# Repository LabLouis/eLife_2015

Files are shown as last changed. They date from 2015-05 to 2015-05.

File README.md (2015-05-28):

Title: Dynamical feature extraction at the sensory periphery guides chemotaxis (manuscript submitted to eLIFE)

Authors: Schulze, A., Gomez-Marin, A., Rajendran, V. G., Lott, G., Musy, M., Ahammad, P., Deogade, A., Sharpe, J., Riedl, J., Jarriault, D., Trautman, E. T., Werner, C., Venkadesan, M., Druckmann, S., Jayaraman, V. and M. Louis

Overview:

This folder contains the scripts for software and design and layout of the hardware associated with the Schulze et al. eLife 2015 manuscript. The repository is organised into five modules corresponding to the specific tools described in the manuscript. Below is a brief description of each module:

1. Electrophysiolgy: Contains scripts associated with the electrophysiology protocols used in the paper.
2. Spike Sorting (OpSIN): Contains scripts and examples associated with the optogenetics-based spike sorting of the electrophysiology data.
3. Tracker Hardware: Contains design files (CAD format) and inventory for the hardware associated with the high-resolution larval tracker.
4. Wormsign: Contains C++ scripts for the software to conduct experiments at the high-resolution larval tracker.
5. Venkman: Independent software module which is used to define the spatial and temporal virtual olfactory environments tested at the larval tracker. This module is coupled to the Wormsign module.

For further details, please find the README file corresponding to each module. For comments/feedback, please e-mail: mlouis_at_crg.eu or matthieu.louis_at_icloud.com

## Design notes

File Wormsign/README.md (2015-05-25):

##Wormsign
####Closed Loop Larva Virtual-Olfaction-Reality System

This software is responsible for the real-time: 

    1) Image analysis with larvae tracking,
    2) Light stimulus delivery, and 
    3) Data acquisition.

######Software Developed By:
Gus K Lott III, PhD, PMP
lottg@janelia.hhmi.org
April 2011

######Software Developed At:
HHMI Janelia Research Campus
19700 Helix Dr.
Ashburn, VA, USA 20147

######Larva Tracker Project Team:
Science: Matthieu Louis, Vivek Jayaraman, Alex Gomez-Marin, Vani Rajendran
Engineering: Gus Lott, Eric Trautman, Lakshmi Ramasamy, Magnus Karlsson, Chris Werner, Pete Davies

For bug reports/comments/feedback, e-mail: mlouis_at_crg.eu or matthieu.louis_at_icloud.com

MAIN.CPP function launches the application GUI (defined in wormsign.h) and sets the windows priority class to REALTIME.  It then initializes the Qt event monitoring loop (in QApplication) which handles button-presses and graphics draw updates, etc.

###The application is structured as several concurrent processes:

    1) Main GUI Thread - defined in wormsign.h
    2) Camera Interface Thread - captures images and does analysis
    3) Stimulus Thread - monitors camera thread for analysis results and sends stimulus
    4) Stage Thread - Communicates with Zaber stages to keep track of current stage position and to track the animal
    5) Experiment Agent Thread - Coordinates the execution of the experiment and carries out data logging

###Wormsign must interconnect with the following systems:

    1) "Venkman" biorules server application (network socket)
    2) Four Zaber Stages (single serial interface)
    3) Stimulus delivery and Camera triggering embedded system (single serial interface)
    4) Basler A622fm Video Camera (IEEE 1394 w/ Basler Pylon Drivers installed)

###This application relies upon the following external software libraries:

    1) Developed under Windows 7 using the windows SDK
    2) Qt v4.7 Application Development Framework
    3) OpenCV v2.2 Computer Vision Library
    4) Basler Pylon v2.3 Camera Interface API

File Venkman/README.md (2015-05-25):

Venkman 

Software Developed By:
Scientific Computing Group
HHMI Janelia Research Campus, Ashburn, VA, USA

For bug reports/comments/feedback, e-mail: mlouis_at_crg.eu or matthieu.louis_at_icloud.com

=======

##Overview

Venkman allows researchers to create “bio-rules” - olfactory experience paradigms based on a larva's current behavior.  
Several bio-rules are supported, enabling a multitude of virtual reality paradigms that broadly fall into categories of time-based, position-based, and/or behavior-based protocols.  
Venkman does this by interfacing with the Wormsign tracking application.  

The following diagram depicts the high level hardware and software components in the system:
 
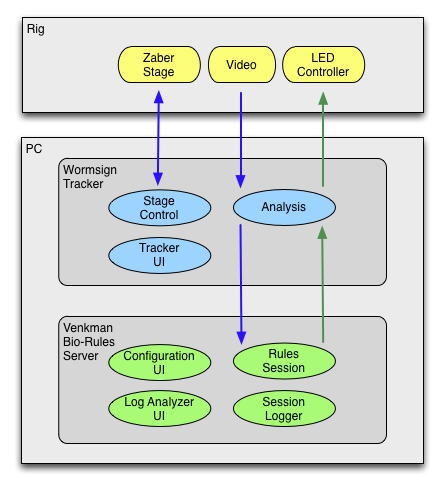
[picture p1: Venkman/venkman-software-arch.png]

 
The bio-rules server accepts body-state measurements such as head, neck and tail positions, head to body angle, and tail bearing from the Wormsign computer vision and tracking algorithm.  
Depending on the VR paradigm chosen by the user for the experiment, these data are used to determine the appropriate stimulus intensity for the current frame.  
The stimulus information is then sent back to Wormsign, which relays the command to the LEDs.
 
##Code / Build Process
 
Venkman is written in Java and was developed using the [IntelliJ IDE](https://www.jetbrains.com/idea/).

IntelliJ should be used to compile and run automated tests.
An ant target 'jar-server' can be used to bundle the compiled results into a jar for deployment.
  
##License

Use is subject to Janelia Research Campus Software Copyright 1.2 license terms 
( [http://license.janelia.org/license/janelia_copyright_1_2.html](http://license.janelia.org/license/janelia_copyright_1_2.html) ).

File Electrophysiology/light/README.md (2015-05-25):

**********************************************
LED_Light_Stimulation.vi: Execution of light stimulation protocols to evoke neural activity in ChR2 expressing neurons according to a preconceived stimulation file (csv format).

By Vani Rajendran and Aljoscha Schulze
Center for Genomic Regulation (CRG), Barcelona Spain
AljoschaTobias@yahoo.com

For bug reports/comments/feedback, e-mail: mlouis_at_crg.eu or matthieu.louis_at_icloud.com
**********************************************

This package contains a Labview routine to drive an LED stimulation according to to a preconceived light stimulation time course (in the form of voltage values defining the light intensity). This stimulation protocol was used in conjunction with one 'NI USB-6008 12-Bit, 10 kS/s Low-Cost Multifunction DAQ' board connected to a PC. The analog output of this DAQ board was connected to the LED driver driving changes of the LED intensity according to the light stimulation protocol.In order to learn the relationship between the output voltage and the light intensity present at the experimental setup, a calibration of the LED as it is connected to the LED controller has to be performed prior to running this routine.

The light stimulation protocol should come in the form of a csv file containing only one column of voltage values. Every line in this csv file corresponds to a voltage and thus a light intensity value of the stimulation time course (values should not exceed 5V). The frame-size (Set frame size) of the execution protocol has to be defined before the stimulation is executed at the Labview VI front panel by the user (units are in milliseconds).

For bug reports/comments/feedback, e-mail: mlouis_at_crg.eu or matthieu.louis_at_icloud.com

**********************************************
Main routines:
**********************************************

* LED_Light_Stimulation.vi: LED stimulation interface

Execution of this program leads to the execution of custom LED stimuli via the analog output port of a Multifunction DAQ device. The stimulus time course (voltage values) of the odor channel has to be computed prior to the execution and saved as a csv file. The user should adapt the stimulation protocol to the frame-size that he intends to use. 

**********************************************
Front panel:
**********************************************

Stimulation START: Pressing this button leads to a prompt asking the user to load the stimulation csv file. As soon as the file is selected the stimulation starts.

Set frame size (min=2ms): Define the frame size of the stimulation protocol in units of milliseconds.

Duration of the Stimulation (s): Shows the duration of the stimulation protocol for the defined frame-size.

Length of csv file: Shows the number of values (each values corresponding to a single frame of the stimulation) contained in the loaded stimulation csv file.

Format of the csv file: The csv file should contain only one column of numbers (voltage values) that correspond to the LED stimulation.

**********************************************
Block diagram:
**********************************************

The user has to open the DAQ Assistant and edit both the coordinates and the analog output port of the DAQ device that is being used to drive the light stimulation via the LED controller.

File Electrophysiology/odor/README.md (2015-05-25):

**********************************************
Odor_stimulation.vi: Execution of odor stimulation protocols to evoke neural activity according to a preconceived stimulation file (csv format).

Software Developed By:
Aljoscha Schulze
Center for Genomic Regulation (CRG), Barcelona, Spain
AljoschaTobias@yahoo.com

For bug reports/comments/feedback, e-mail: mlouis_at_crg.eu or matthieu.louis_at_icloud.com
**********************************************

This package contains a LabView routine to drive a dynamic air-flow/odor stimulation according to a preconceived odor stimulation time course that contains voltage values defining the corresponding to the air-flow in each channel. The stimulation execution is defined in such a way as to have the combined flow of both channels never exceed a predefined value. As a result the combined flow of both channels is kept constant.

This two channel stimulation protocol was used in conjunction with one 'NI USB-6008 12-Bit, 10 kS/s Low-Cost Multifunction DAQ' board connected to a PC. Each of the two analog outputs of this DAQ board was connected to an air-flow controller driving changes of the air-flow according to the loaded stimulation protocol. In order to learn the relationship between the output voltage and the achieved air-flow/odor concentration a calibration of the flow controller (by measuring the air-flow and/or the resulting odor concentration) has to be performed before running this routine. 

The odor stimulation protocol has to come in the form of a csv file containing one column of voltage values (corresponding the values driving the air-flow controller of the odor channel). Every line in this csv file corresponds to a voltage and thus a flow value of the odor stimulation (values should not exceed 5V). The frame-size (Set frame size) of the execution protocol has to be defined before the stimulation is executed at the LabView VI front panel by the user (units are in milliseconds).

**********************************************
Main routines:
**********************************************

* Odor_stimulation.vi: Two channel odor stimulation interface

Execution of this program leads to the execution of custom air-flow/odor stimuli via two channels of the analog output port of a Multifunction DAQ device. The stimulus time course (voltage values) has to be computed prior to the execution and saved as a csv file. The empty channel is continuously computed by subtracting the voltage values of the odor channel from the user defined maximum flow rate. The user should adapt the stimulation protocol (csv file) to the frame-size that he intends to use.

**********************************************
Front panel:
**********************************************

Stimulation START: Pressing this button leads to a prompt asking the user to load the stimulation csv file. As soon as the file is selected the stimulation starts.

Set frame size (min=2ms): Define the frame size of the stimulation protocol in units of milliseconds.

Set maximum voltage: Define the voltage corresponding to the combined flow of channel 1 + channel 2. As a result the flow will always be kept at this constant value throughout the stimulation.

Duration of the Stimulation (s): Shows the duration of the stimulation protocol for the defined frame-size.

Length of csv file: Shows the number of values (each values corresponding to a single frame of the stimulation) contained in the loaded stimulation csv file.

Format of the csv file: The csv file should contain only one column of numbers (voltage values) that define the flow rate of the odor-channel. The values driving the complementary (empty) channel are derived by subtracting the odor channel from the defined overall flow ('maximum voltage').

**********************************************
Block diagram:
**********************************************

The user has to open the DAQ Assistant and edit both the coordinates and the analog output port of the DAQ device that is being used to drive the light stimulation via the LED controller.

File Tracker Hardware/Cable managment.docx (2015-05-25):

The purpose of this document is to document the umbilical handling and support system used for the larva tracker. The following pictures show the umbilical handling approach. A cable guide by IGUS was used to control the camera and blue LED lighting cables (model number of the cable guide is provided in the BOM).

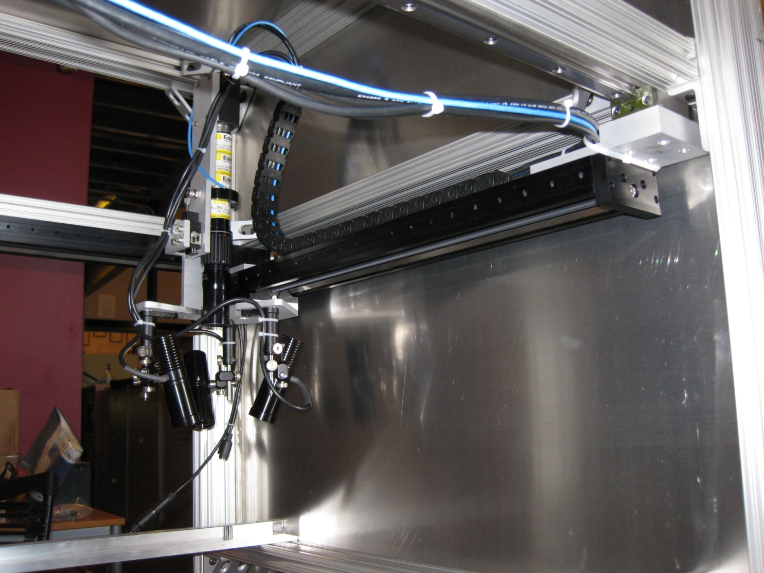
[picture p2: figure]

IGUS Cable guide was attached to and resting on the top side of the Zaber rail. The guide was anchored to the Zaber at this point.

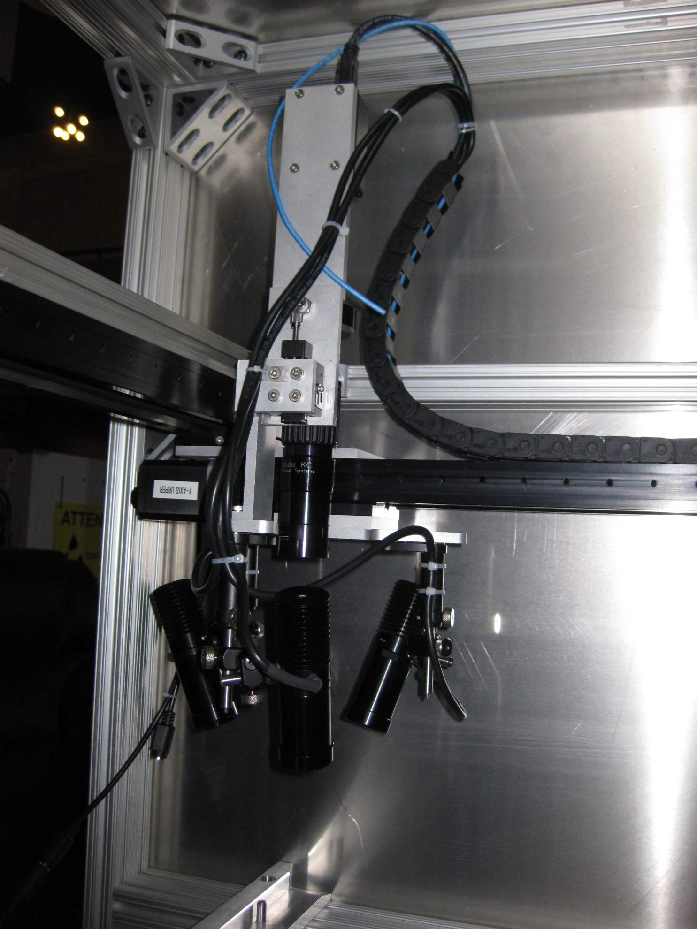
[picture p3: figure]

A two conductor, shielded wire was added to the assembly to trigger the camera (per HHMI request).

Cabling was tie-wrapped and anchored to mounting plates for strain relief.

IGUS Cable guide was about 20 inches long.

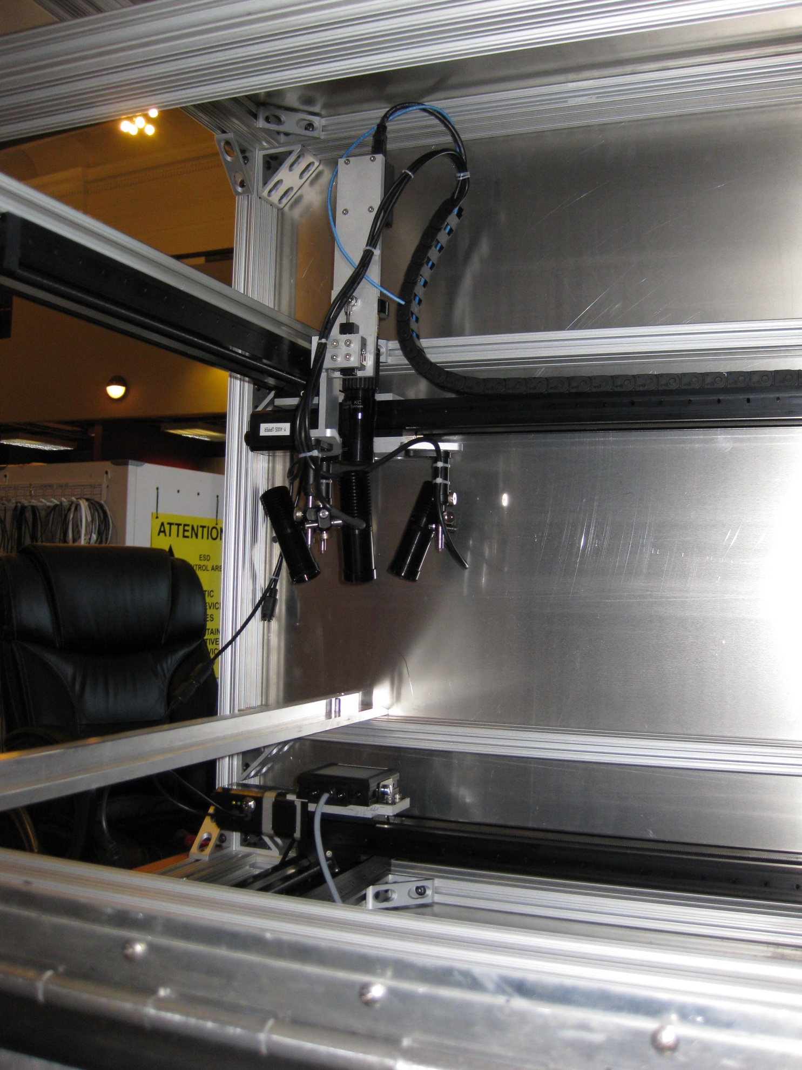
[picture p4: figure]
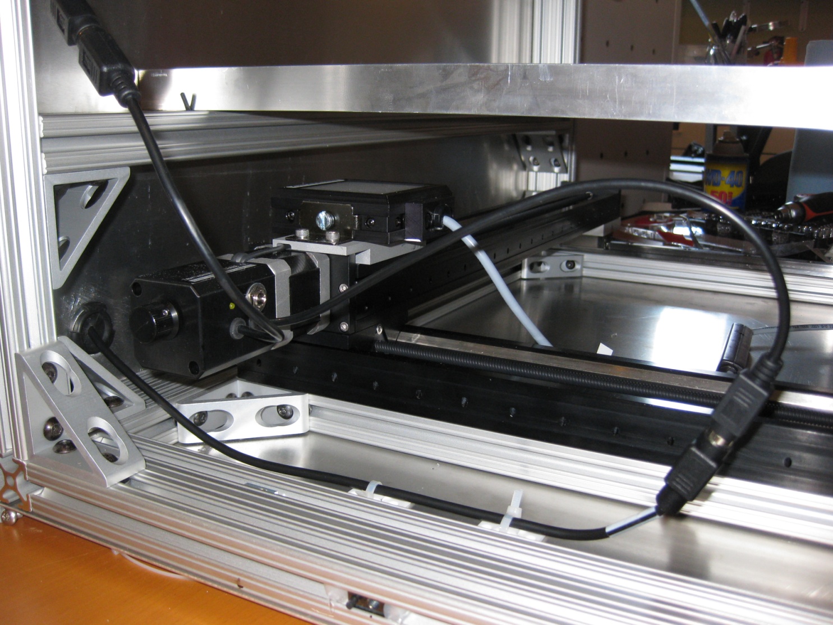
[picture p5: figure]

Panel LED backlight excess cabling was allowed to sit on the bottom of the assembly with no special handling provisions.

The Zaber drives were daisy-chained per Zaber. Only two Zaber drives were inside the housing (the upper and lower ‘Y’ drives). The lower ‘Y’ drive was powered from a line that came into the back wall (through a rubber grommet) as shown. The lower ‘Y’ drive was daisy-chained to the upper ‘Y’ drive.

Form Revision 2/6/08 Form F-0018 Confidential p. 4 of 4

FORM REVISION 6/24/09 Page 1 of 4 Form F-0018 www.keytechinc.com This document contains work product that is confidential or proprietary to Key Tech and affiliated companies. Neither this document nor the material herein is to be reproduced, distributed, or disclosed in whole or in part, except as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

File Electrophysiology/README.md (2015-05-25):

This package contains LabVIEW routines to drive the dynamic air-flow/odor stimulation and light stimulation according to a preconceived odor/light stimulation time course.

Software Developed By:

Aljoscha Schulze
Center for Genomic Regulation (CRG), Barcelona, Spain
AljoschaTobias@yahoo.com

For bug reports/comments/feedback, e-mail: mlouis_at_crg.eu or matthieu.louis_at_icloud.com

The folder ‘odor’ contains the following:

1.	LabVIEW script (.vi format) – Main LabVIEW script.
2.	Description file (.rtf format) – Detailed explanation of the LabVIEW script and the LabVIEW interface.
3.	Graphical description file (.pdf format) – Graphical explanation of the LabVIEW interface and the block diagram for the LabVIEW script.
The folder ‘light’ contains the following:
1.	LabVIEW script (.vi format) – Main LabVIEW script.
2.	Description file (.rtf format) – Detailed explanation of the LabVIEW script and the LabVIEW interface.
3.	Graphical description file (.pdf format) – Graphical explanation of the LabVIEW interface and the block diagram for the LabVIEW script.

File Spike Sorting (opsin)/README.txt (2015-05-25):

**********************************************
OpSIN: Opto-genetic spikesorting and identification of neurons
**********************************************

This package contains various Matlab routines for extracting spike events associated with Channelrhodopson (ChR2) targeted neurons of interest.

For bug reports/comments/feedback, e-mail: parvez@ieee.org

To download the latest version of OpSIN, please visit: https://github.com/pahammad/OpSIN

**********************************************
Main routines:
**********************************************

* OpSIN_SS_1Ch_batchWithGuisNew: semi-supervised spikesorting tool

This is the main entry point of the OpSIN algorithm. This tool is a combination of automated processing and manual annotation, to enable fast processing of single channel e-phys recordings. The automated processing allows the user to quickly divide the spike candidate pool into three categories: good/unsure/bad. Once this determination is made, the user is guided through the unsure set of spike candidates to finalize the spike annotation.

**********************************************
Useful sub-routines:
**********************************************

1. Benchmarker_MoMa_1Ch_batch: Mostly manual benchmarking tool

This tool is useful to generate expert-annotated ground-truth for single-channel e-phys recordings from a loose-patch or suction-electrode type preparation. The assumption is that one or a few neurons of interest are tagged with ChR2. It is the slowest of the available options in OpSIN package, but it is also the most objective approach to generate expert-guided ground-truth data.

Several other useful subroutines can be found in the Extra Goodies subfolder.

**********************************************
Example Walkthrough: “Using_OpSIN.m”
**********************************************

This is an example to walk through a case scenario for OpSIN based processing of optogenetic spike-sorting of ephys (electrophysiology) signals.

A) To be done before you run OpSIN

A1) The example datafile '100W_constant_light_stimulation_example_01' contains the recorded electrophysiology data (20kHz sample rate) in column 1, and the voltage trace used for the light stimulation in column 3.

A2) Copy the example datafile into a new folder and specify the directory by the variable name 'generalDataRootDirectory'

A3) You will have to specify the voltage value that was used during the pre-stimulation pulses to aid the spike selection process performed by the algorithm. The variable is called: 'lightChannelONlevel'

B) Run OpSIN

B1) Run'OpSIN_SS_1Ch_batchWithGuis.m' 
A window will open asking you to select the file you want to spike sort. Select the example file '100W_constant_light_stimulation_example_01'.

you will be asked to enter '1' to continue the analysis:
'Enter 1 to continue:' Enter '1' and press return.

B2)
Two graphs will popup as a result of the algorithm looking for possible spike candidates during pre-stimulation pulses.

One graph contains all candidate spike waveforms that were found by the algorithm during light stimulation periods.

The second graph shows candidate spike waveforms clustered together to allow the user to combine relevant clusters that contain the spike waveform of interest (representing ChR2 evoked activity). 

You will be asked to enter the number of CLEAN cluster template IDs to pool together"
'Enter the number of CLEAN cluster template IDs you want to pool together:'
Enter the number of clusters you would like to include and press return.

You will have to select clusters based on visual inspection of the spike shape. Your selection should include the cluster containing the one containing the highest number of spike waveforms.

B3)
You will be asked to specify the cluster ID(s) on which you like to base the template matching:
'Enter the BEST clean template waveform ID, ideally one centered on first peak (for double-bump spikes):'

You will be asked whether the chosen cluster contains spikes which were centered on the thin peak or the broad peak:
 For double bumps: was your first template choice centered (~40-50) on the thin peak? (0 = No; 1 = Yes)
Enter '0' and press return.

B4) 

A GUI will pop up (SELECT SPIKE DETECTION THRESHOLD) asking you to specify the spike detection threshold specific to this recording.
Once you adjusted the 'SD section threshold' bar using the mouse, press the 'FINALIZE'
button.

B5)

You will be asked to specify whether the electrophysiology data contains double bump spikes, or not:
'Enter 1 if the data contains double bump spikes, 0 otherwise:'
Enter '0' and press return.

B6)

A GUI will pop up (SELECT THRESHOLDS FOR GOOD, UNSURE & BAD SPIKES), asking you to specify both the 'GOOD' and 'BAD' spike Threshold in the context of a 'Spike Probability Histogram' that indicates the probability distribution of all detected spike candidates (lower right graph). A high probability value reflects a good fit the   spike template.
On the upper right you can also see all 'Estimated spike probabilities' as they are distributed throughout the entire recording. The red trace shows the voltage signal of the light stimulation.

The upper left graph shows all the spikes that - with the currently selected probability threshold - are defined as 'Good Spikes' by the algorithm.

The middle left graph shows all spikes that - with the currently selected probability threshold - are considered as borderline (unsure) spikes. Once that the probability threshold is defined by the user, all spikes that are contained in here will each be manually checked by the user whether they fit the template of a ChR2 evoked spike, or not.

The lower left graph contains all spikes that - with the currently selected probability threshold - are considered 'Bad Spikes' by the algorithm and will accordingly not be included as ChR2 evoked spike candidates.

The probability threshold should be set such as to exclude all spike waveforms that are not in agreement with the template spike waveform. To this end, a thorough visual inspection of all three candidate spike pools is required with the goal to keep the 'Good Spikes' pool (upper left graph) as homogenous as possible. More spikes in the middle panel mean a long user assisted spike selection process.

Once the probability threshold bar by using the mouse press the 'finalize' button.

B7)

In case you kept some spike waveforms in the unsure spike waveform pool you will be asked to decide for every single uncertain spike candidate whether to include it or not.

'Enter your input (1 = highConf good spike, 11= lowConf good spike, 2= highConf bad spike, 22= lowConf bad spike (default), -1=undo):' 

enter '1' if you want to include a spike
enter '2' if you want to discard a spike

B8)

Once this is done for all uncertain spike candidates the algorithm is finished.

The final sorted dataset is saved under the original filename plus '_OpSIN' and the current date.

The final spike data (1 represeting a spike, 0 representing no spike) is saved in the fourth column of the final dataset.

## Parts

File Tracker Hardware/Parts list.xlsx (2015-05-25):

Materials / Description | Part No. | Qty | Vendor | Comments / questions:
ELECTRONICS
Motorized linear stage 450 mm travel - kit | KT-LSR450B | 4 | Zaber
Motorized linear stage 450 mm travel | T-LSR450B |  | Zaber
Data cable - 6 ft | T-DC06 |  | Zaber
Power supply substitution | SUB-PS15V0440 |  | Zaber
3 axis Joystick | T-JOY3 | 1 | Zaber
Passive X stage | SR15W1SS | 2 | THK
IF2 OBJECTIVE | NT53-782 | 1 | Edmund Optics
KC/S VIDEO MICROSCOPE | NT53-785 | 1 | Edmund Optics
25MM FILTER HOLDER | NT53-788 | 1 | Edmund Optics
HI PERFORMANCE LONGPASS FILTER | NT62-983 | 1 | Edmund Optics
BASLER 622F CAMERA | NT58-297 | 1 | Edmund Optics
Edmund Optic Clamp on Camera | NT52-930 | 1 | Edmund Optics
Red backlight | BL0202-660IC | 1 | Advanced Illumination
White backlight | BL0202-WHIIC | 1 | Advanced Illumination
Blue LED light source / light guide | LCS-0470-03-22 | 3 | Mightex
Blue LED lens | ACC-LCS-F-25-100 | 3 | Mightex
Blue/Green LED power Supply / Controller | SLA-1200-2 | 2 | Mightex
Custom LED controller from ID&F | JF-VJ-LT0002 | 1 | HHMI
Filter Holders for LEDs | JF-VJ-LT0002 | 4 | HHMI
Software Engineering | - | 1 | HHMI
Blue bandpass filter | 48-075 | 3 | Edmund Optics | Mounts over blue LEDs
Green LED | LCS-0530-05-22 | 1 | Mightex
Green filter in optical path | 32-755 | 1 | Edmund Optics | Install in optical path (inside of NT-53-788) on top of the red filter
KEY TECH HARDWARE
Rail for Glass Plate Assy | DMP-211003-0001 | 2 | Bruce Machine, Baltimore, MD 410-752-5046
8020 Assembly, Including Leveling Feet, Gussets, Hardware | DMA-211003-0001 | 1 | Penn-Air & Hydraulics | Includes all 8020 frames, drop-in T-Nuts & hardware. See Penn-Air quote in "Penn-Air" Tab.
8020 1x2, 28in | DMP-211003-0002 | 6 | Penn-Air & Hydraulics
8020 1x2, 23in | DMP-211003-0003 | 9 | Penn-Air & Hydraulics
8020 1x2, 30.375in | DMP-211003-0004 | 4 | Penn-Air & Hydraulics
8020 1x2, 30in | DMP-211003-0005 | 2 | Penn-Air & Hydraulics
1/4-20 x .5" BHSCS | 3061 | As Nec | Penn-Air & Hydraulics
Double Econ T-Nut, 1/4-20 THD | 3280 | As Nec | Penn-Air & Hydraulics | For securing gussets, etc
Drop In T-Nut 10-32 | 3375 | As Nec | Penn-Air & Hydraulics | For securing sheet metal, other components to enclosure
6 Hole 90 Deg Joining Plate | 4061 | As Nec | Penn Air & Hydraulics | For upper frame assy
3 Hole Slotted Corner Bracket | 4250 | 2 | Penn Air & Hydraulics | Used to support upper 8020 plane in back right corner of assy to prevent interference with THK slider. Secure with 1/4-20 hardware
M4 Drop-In T-Nut | 14164 | As Nec | Penn-Air & Hydraulics | To secure THK rails
M6 drop-in Nut | 3876 | As Nec | Penn-Air & Hydraulics | Secure bottom X Zaber to Rail
Bottom Slider Bracket | DMP-211003-0006 | 1 | FirstCut (http://www.firstcut.com/)
LED Bracket | DMP-211003-0007 | 1 | FirstCut (http://www.firstcut.com/)
Camera Bracket | DMP-211003-0008 | 1 | FirstCut
Zaber Bracket Flat | DMP-211003-0009 | 1 | FirstCut
Stepped Zaber Bracket | DMP-211003-0010 | 1 | FirstCut (http://www.firstcut.com/)
Back Sheet | DMP-211003-0011 | 1 | Warren Ehret (410) 752-4922
Bottom Sheet | DMP-211003-0012 | 1 | Warren Ehret (410) 752-4923
Front Sheet | DMP-211003-0013 | 1 | Warren Ehret (410) 752-4924
Top Sheet | DMP-211003-0014 | 1 | Warren Ehret (410) 752-4925
Side Sheet | DMP-211003-0015 | 2 | Warren Ehret (410) 752-4926
Camera Mount | DMP-211003-0016 | 1 | FirstCut (http://www.firstcut.com/)
Glass Frame | DMP-211003-0017 | 2 | Bruce Machine, Baltimore, MD 410-752-5046
Glass Plate | DMP-211003-0018 | 2 | Mirror Crafters (410 947-0900) for 3/8 in tempered…OR S.I. Howard Glass Co (508 753-8146) for borofloat glass non-tempered
Door Spacer | DMP-211003-0019 | 2 | Key
Door | DMP-211003-0020 | 1 | A&E Mfg (http://www.ae-mfg.com/)
LED Plate | DMP-211003-0021 | 1 | FirstCut (http://www.firstcut.com/)
Door Hinge | DMP-211003-0022 | 1 | Key (Machine from MMC Part 1581A167)
COTS HARDWARE
Cable Track, Approx 20" | 07-20-038-0 | 2 | IGUS (http://www.igus.com/igus/wech4_i.asp?part=07-20-038-0&series=07&group=E-Chain%20E2%20Micro)
Cable Track Mounting Bracket | 060-20-12PZ | 1 | IGUS
Handles | 1948A4 | 4 | MMC | Components enough for two glass plate assys
Door Magnet | 1745A12 | 2 | MMC
Door Foam (Interior) | 93085K162 | 10" | MMC
Door Foam (Exterior) | 8694K54 | 25" | MMC
6mm Translation Stage | MS1/M | 1 | Thor | Remove 2-56 set-screw, and replace with MMC 90128A042
Thor Swivel | MSWC | 3 | Thor | Lock with Loctite when final LED positioning is determined
Thor Mini-Post | MSH2 | 3 | Thor | Lock with Loctite when final LED positioning is determined
Mini Post, 3" | MS3R | 3 | Thor | Lock with Loctite when final LED positioning is determined
Mini Post, 1" | MS1R | 3 | Thor | Lock with Loctite when final LED positioning is determined
Thread Adaptor | MSA8 | 3 | Thor | Lock with Loctite when final LED positioning is determined
Plastic Plug, Round | 9688K131 | 2 | MMC | To close off viewing holes in side panels
M6 Socket-Head Cap Screws, 6mm | 91290A310 | As Nec | MMC | To Secure Zabers to Blocks
M6 Socket-Head Cap Screws, 8mm | 91290A312 | As Nec | MMC | To Secure LED Bracket to Zaber Carriage
M6 Socket-Head Cap Screws, 12mm | 91290A319 | As Nec | MMC | To Secure Glass Frame Rails to 8020 hardware
M6 Pan-Head Screws, 8mm | 91239A314 | As Nec | MMC | To Secure Upper X Zaber to Upper Y Zaber on Zaber Bracket_Flat (Need pan-head due to potential interference)
M4 Socket Head Cap Screw, 5mm | 91290A138 | As Nec | MMC | To secure BL0202 LED to LED Bracket
M4 Socket Head Cap Screw, 12mm | 91292A117 | As Nec | MMC | To Secure THK Rails
M4 Socket Head Cap Screw, 10mm | 91292A116 | As Nec | MMC | To Secure ThorLabs MS1/M 1cm adjuster to Camera Bracket, and Camera Mount to Basler Camera
M4 Flat-Head Screw, 6mm | 91294A186 | 1 | MMC | To Secure MS1/M to Camera Mount
M4 Flat-Head Screw, 8mm | 91294A188 | 8 | MMC | To secure Magnet Latches to Door
M4 Flat-Head Screw, 16mm | 91294A194 | 4 | MMC | To secure Magnet to Front Panel
M4 Nut with Lock Washer | 93825A120 (http://www.mcmaster.com/) | 4 | MMC | To secure flat screw and Magnet latch to door
1/4"-20 Socket Head Cap Screw, 5/16 long | 91251A534 | 1 | MMC | To secure to C-clamp around camera assy
M5 Socket Head Cap Screw, 6mm | 91239A220 (http://www.mcmaster.com/itm/find.ASP?tab=find&context=psrchDtlLink&fasttrack=False&searchstring=91239A220) | As Nec |  | To secure hinge to Door
10-32 Socket Head Cap Screw, 7/16" | 92949A264 | 6 | MMC | To secure hinge to front panel via 10-32 drop-in nuts
2-56 Socked Head Cap Screw, 1/4" | 90128A042 | 1 | MMC | Replace 2-56 pan-head screw provided with MS1/M, for ease in adjusting screw
Cable ties Adhesive-back tie-downs | MMC Misc |  | MMC
Assembly Drawings
Top-Level Assy | DMA-211003-0001 | 1
Glass Plate Assy | DMA-211003-0002 | 1

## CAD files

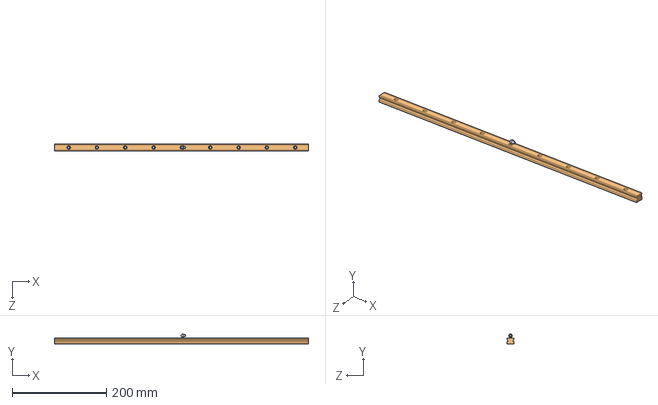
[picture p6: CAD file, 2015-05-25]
Tracker Hardware/Mechanical Design Source Code/Solid Works Assembly/THK Rail and Guide.SLDASM
538.0 x 21.7 x 15.0 mm
grease plug
THK Rail

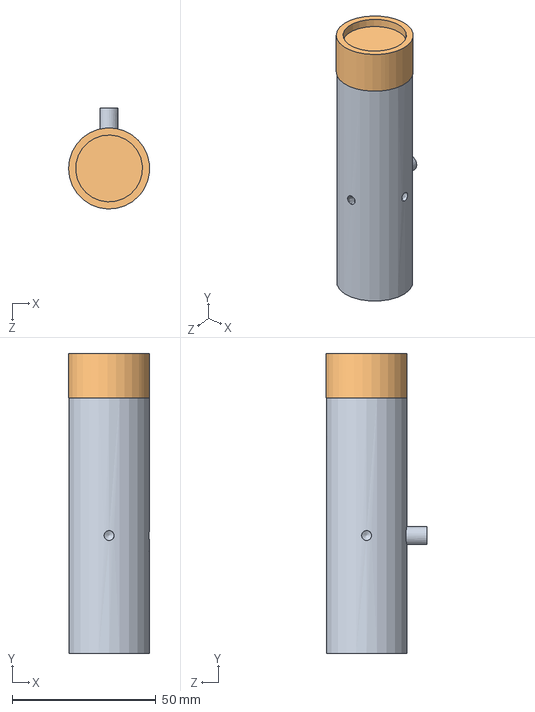
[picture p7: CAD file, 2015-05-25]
Tracker Hardware/Mechanical Design Source Code/Solid Works Assembly/Mightex LED Assy.SLDASM
28.1 x 104.3 x 35.1 mm
Mightex_LED
Mightex_Focusing Module

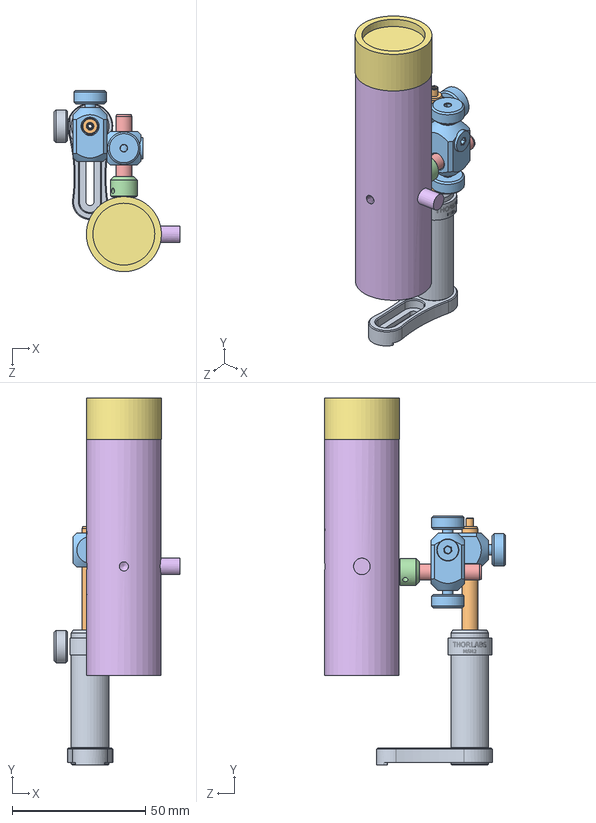
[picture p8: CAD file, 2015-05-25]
Tracker Hardware/Mechanical Design Source Code/Solid Works Assembly/Mini Series LED Assy.SLDASM
47.2 x 137.9 x 68.1 mm
8587-E0W
8579-E0W
13441-E0W x 2
11899-E0W
8573-E0W
Mightex_LED
Mightex_Focusing Module

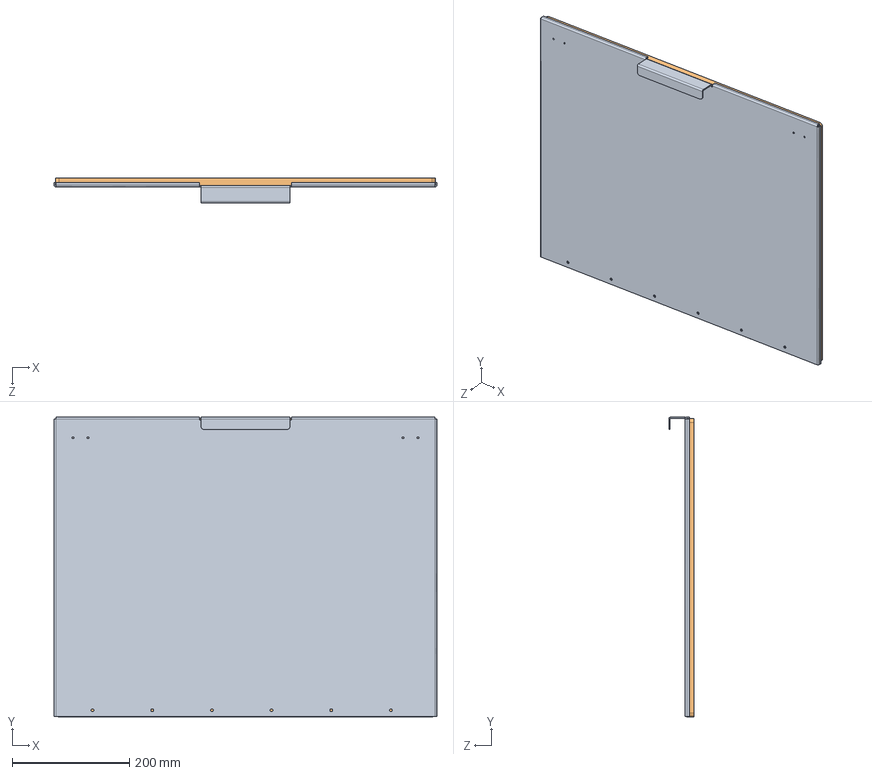
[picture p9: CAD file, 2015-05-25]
Tracker Hardware/Mechanical Design Source Code/Solid Works Assembly/Door Assembly.SLDASM
652.3 x 510.6 x 43.2 mm
Door
Door Gasket

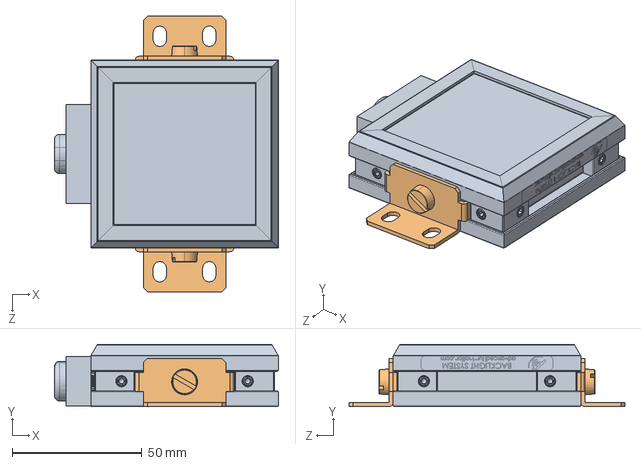
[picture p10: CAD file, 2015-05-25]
Tracker Hardware/Mechanical Design Source Code/Solid Works Assembly/BL0202 Assy.SLDASM
86.3 x 23.9 x 106.1 mm
BL020201
BL Mounting Hardware x 2

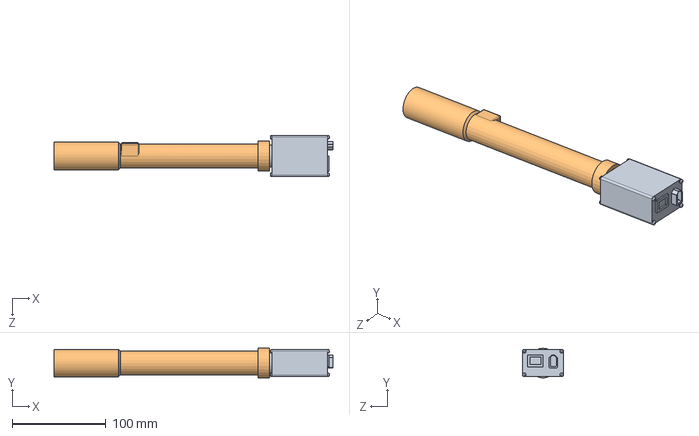
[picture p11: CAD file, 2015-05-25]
Tracker Hardware/Mechanical Design Source Code/Solid Works Assembly/Camera and Lens.SLDASM
298.0 x 31.6 x 44.0 mm
Camera Body
Lens Camera

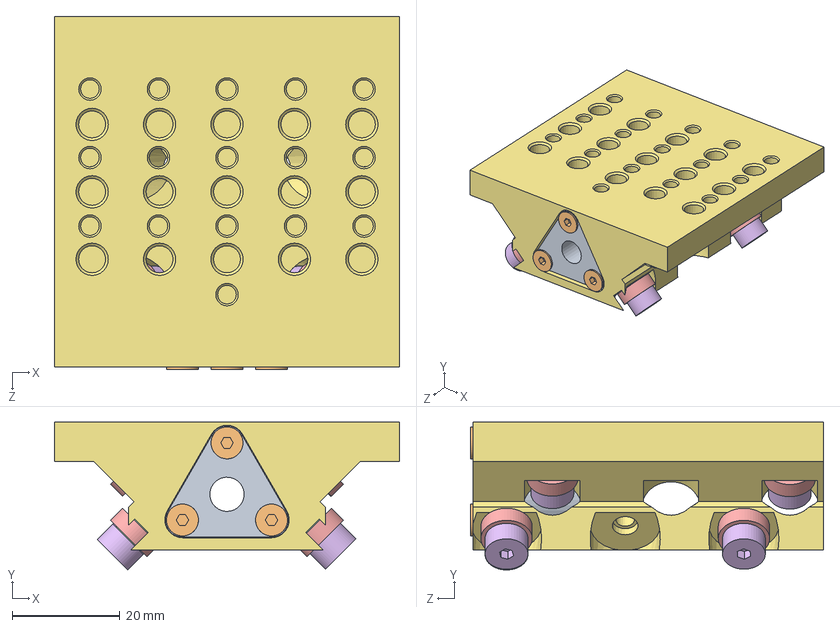
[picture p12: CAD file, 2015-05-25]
Tracker Hardware/Mechanical Design Source Code/Solid Works Assembly/Car sub assy.sldasm
64.0 x 27.4 x 65.4 mm
Lead Screw Nut
Screw_M3x12 CS x 3
Washer_5-32ID
Bearing Washer x 8
3%8 in bearing x 8
ShoulderScrew x 8
T-LSR Top

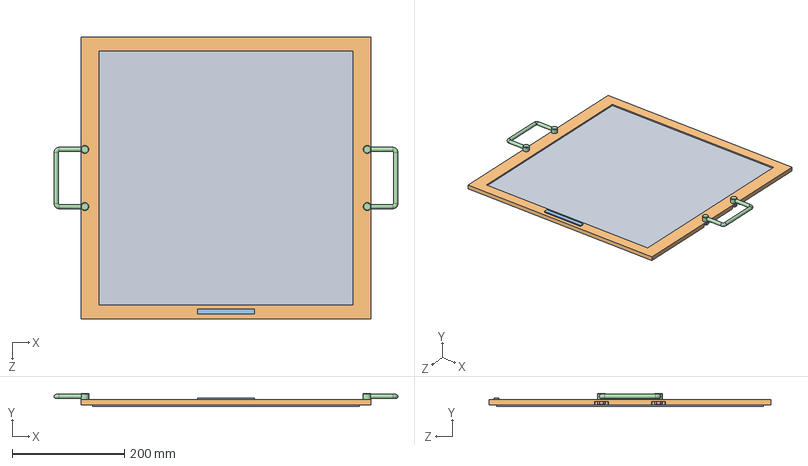
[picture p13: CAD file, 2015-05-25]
Tracker Hardware/Mechanical Design Source Code/Solid Works Assembly/Glass plate assembly.SLDASM
611.6 x 23.8 x 502.1 mm
Glass Plate
glass frame
label
handle for glass plate x 2
5-16 24 nut mmc 94945A215 x 4

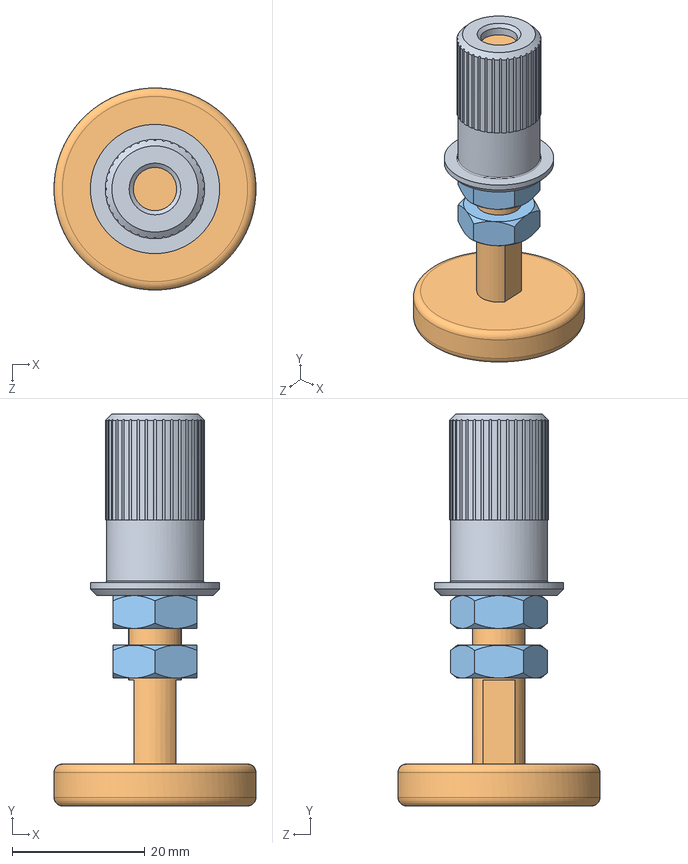
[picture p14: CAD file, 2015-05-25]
Tracker Hardware/Mechanical Design Source Code/Solid Works Assembly/Leveling Feet Hardware.SLDASM
30.5 x 59.2 x 30.5 mm
Rexroth-Insert with 5_16 thrd
Rexroth-Leveling Glider Foot-5_16 stud
HJNUT 0.3125-18-D-N x 2

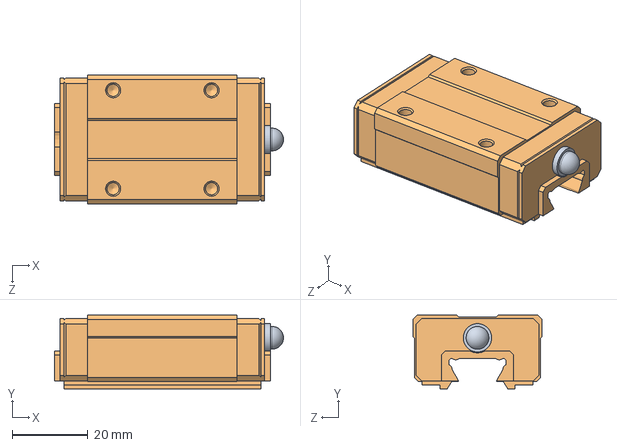
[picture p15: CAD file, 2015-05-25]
Tracker Hardware/Mechanical Design Source Code/Solid Works Assembly/THK car.sldasm
60.5 x 19.5 x 34.0 mm
grease plug
THK SR-15W

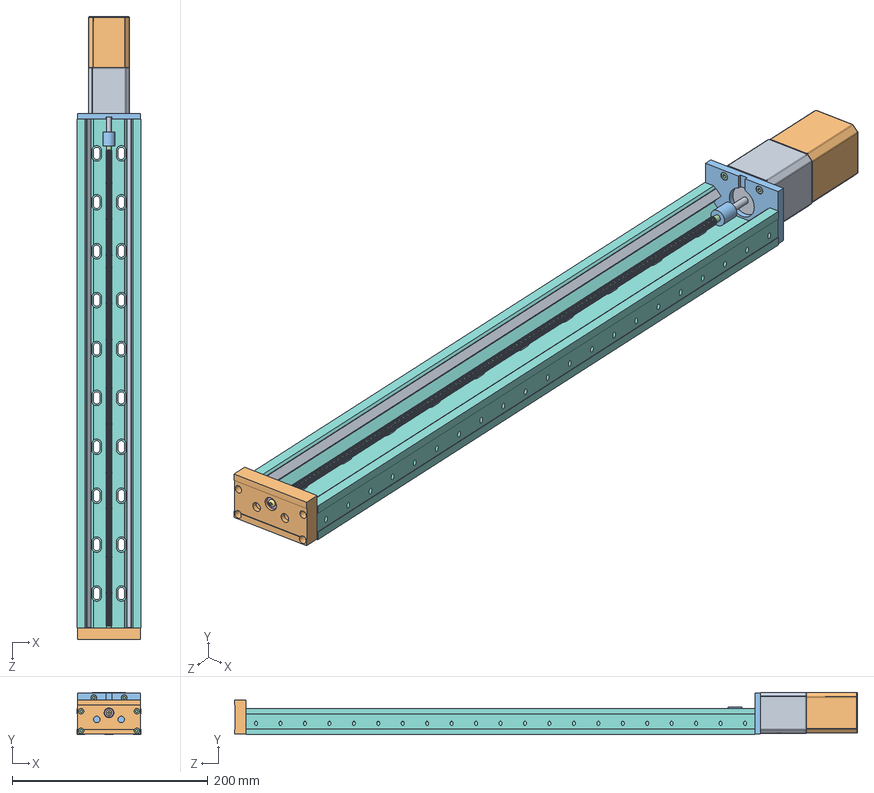
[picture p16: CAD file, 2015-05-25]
Tracker Hardware/Mechanical Design Source Code/Solid Works Assembly/T-LSR450.SLDASM
65.0 x 43.3 x 637.0 mm
NM17-H
T-NM17 Housing
Coupling_CPS12
T-LSR450 Lead Screw
Screw M3 x 6 set screw x 18
Bearing_Thrust_4-8-4 x 2
Screw_M3 x 5 Button Cap
T-LSR450 Base
T-LSR450 Compression Bar x 2
T-LSR Bearing End Plate_Thrust Bearing Version1
Motor Mount End Plate
Screw M3 x 8 SC x 12

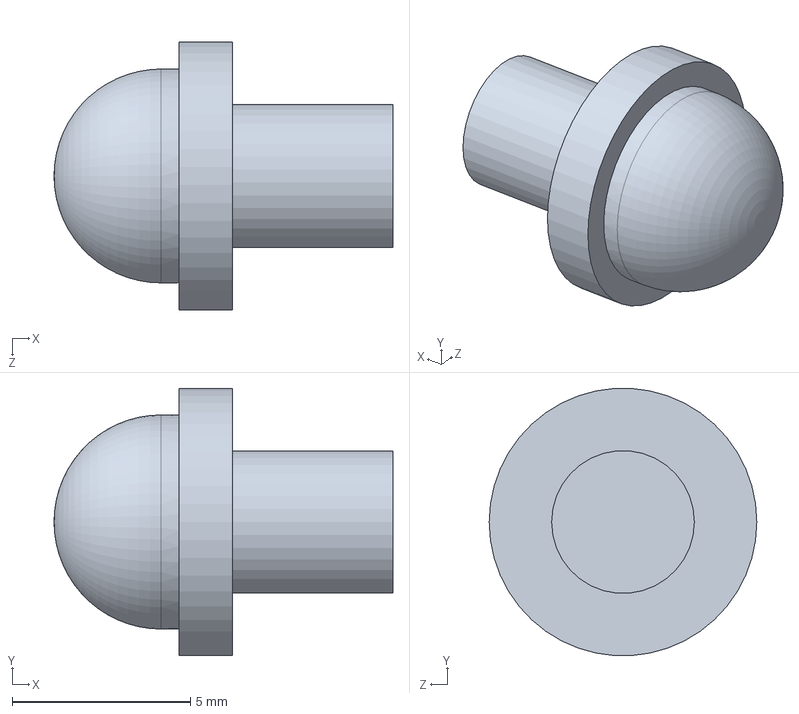
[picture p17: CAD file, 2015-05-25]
Tracker Hardware/Mechanical Design Source Code/Solid Works Parts List 1/grease plug.SLDPRT
9.50 x 7.48 x 7.50 mm

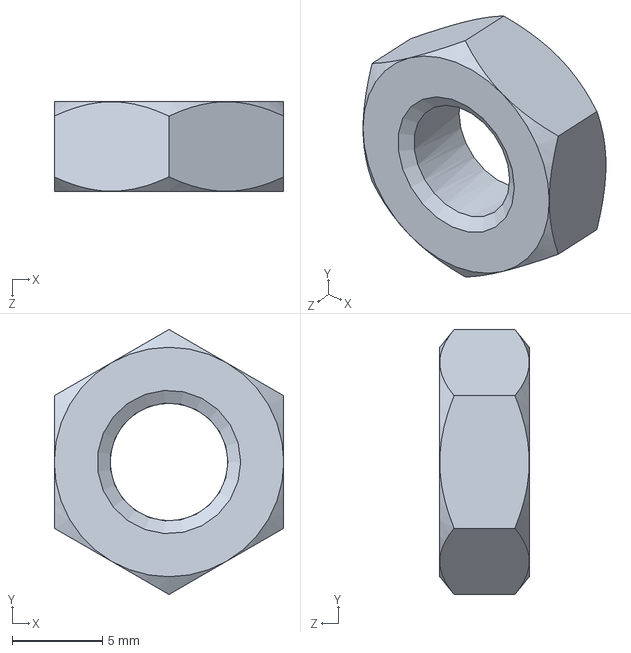
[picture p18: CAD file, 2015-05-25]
Tracker Hardware/Mechanical Design Source Code/Solid Works Parts List 2/HJNUT 0.3125-18-D-N.sldprt
12.7 x 14.7 x 4.95 mm

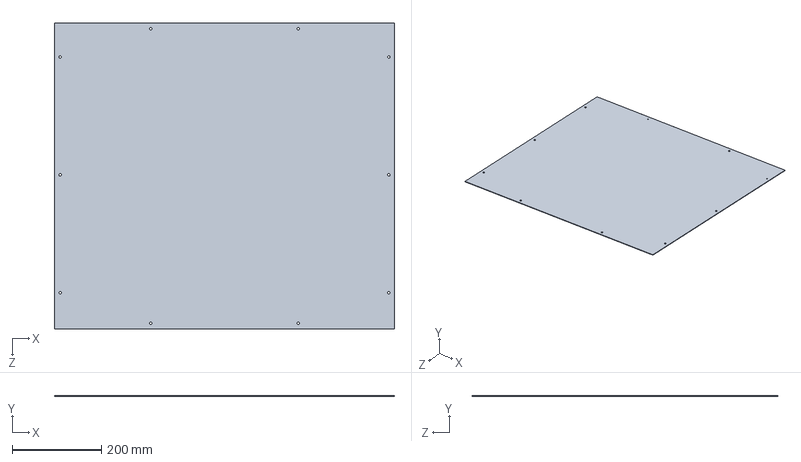
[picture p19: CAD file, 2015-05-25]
Tracker Hardware/Mechanical Design Source Code/Solid Works Parts List 1/Top Sheet .SLDPRT
762.0 x 1.59 x 685.8 mm

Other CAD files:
Tracker Hardware/Mechanical Design Source Code/Solid Works Parts List 2/8020_2128.SLDPRT
Tracker Hardware/Mechanical Design Source Code/Solid Works Parts List 1/Bottom Slider Bracket.SLDPRT
Tracker Hardware/Mechanical Design Source Code/Solid Works Parts List 2/handle for glass plate.SLDPRT
Tracker Hardware/Mechanical Design Source Code/Solid Works Parts List 1/Door Gasket.SLDPRT
Tracker Hardware/Mechanical Design Source Code/Solid Works Assembly/ThorLabs LED Assy.SLDASM
Tracker Hardware/Mechanical Design Source Code/Solid Works Parts List 1/11899-E0W.sldprt
Tracker Hardware/Mechanical Design Source Code/Solid Works Parts List 1/13441-E0W.SLDPRT
Tracker Hardware/Mechanical Design Source Code/Solid Works Parts List 1/1581A167_Hinge.SLDPRT
Tracker Hardware/Mechanical Design Source Code/Solid Works Parts List 1/1745A12_bracket.SLDPRT
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

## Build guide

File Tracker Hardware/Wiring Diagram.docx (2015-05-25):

# Wiring Diagram

Note: See Bill of Materials document for LED information.

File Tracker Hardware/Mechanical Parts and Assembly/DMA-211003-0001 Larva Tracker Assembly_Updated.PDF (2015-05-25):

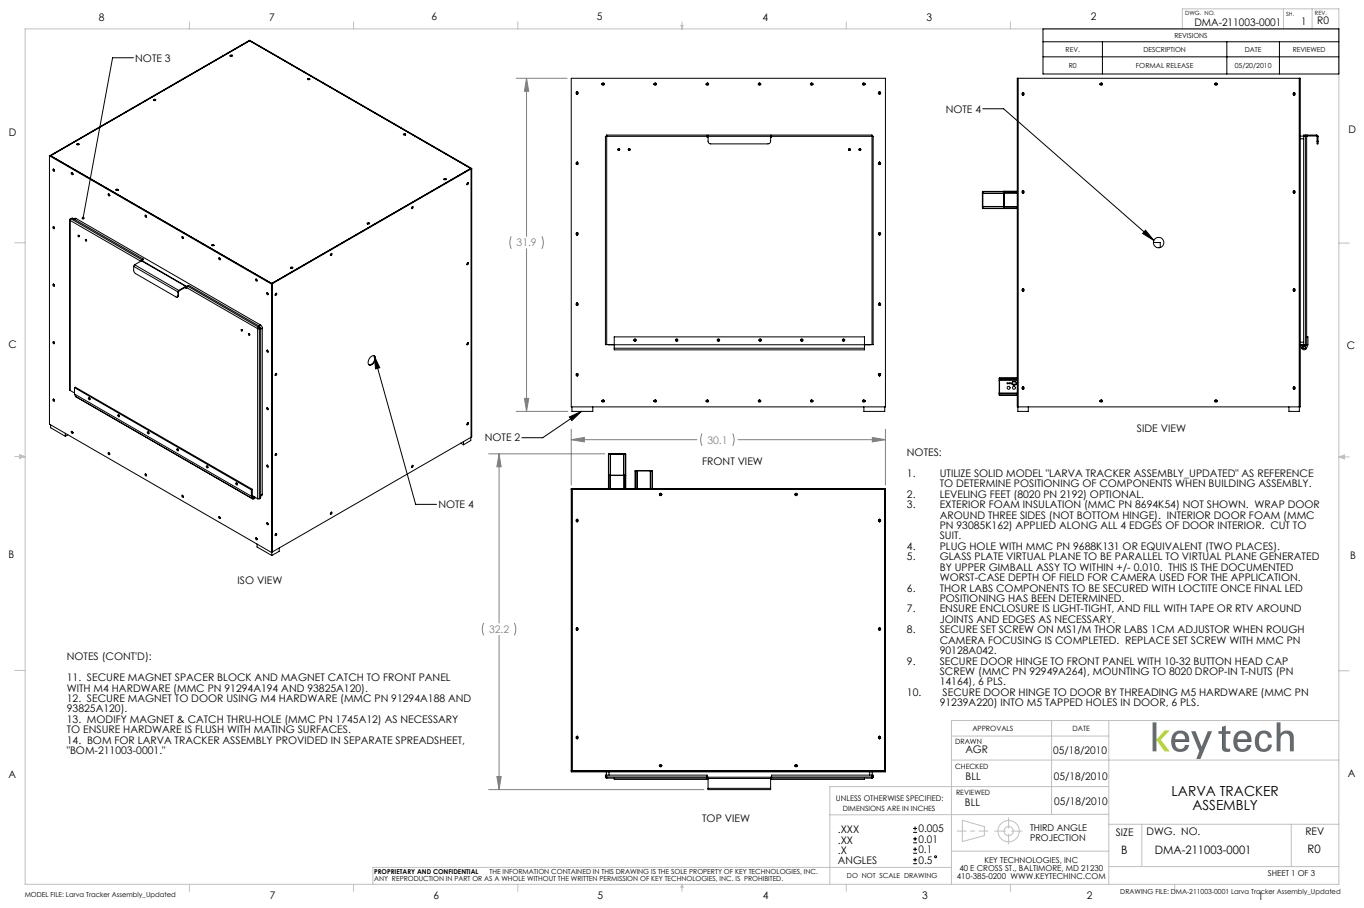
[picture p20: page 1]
NOTE 3; NOTE 4; NOTE 2; TOP VIEW; FRONT VIEW; SIDE VIEW; ISO VIEW; DWG. NO.; REV; SHEET 1 OF 3; MODEL FILE: Larva Tracker Assembly_Updated; DRAWING FILE: DMA-211003-0001 Larva Tracker Assembly_Updated; DMA-211003-0001; 1 R0 DWG. NO.; REV.; LARVA TRACKER ASSEMBLY 05/18/2010; THIRD ANGLE

REV. | DESCRIPTION | DATE | REVIEWED
R0 | FORMAL RELEASE | 05/20/2010

NOTES:
1. UTILIZE SOLID MODEL "LARVA TRACKER ASSEMBLY_UPDATED" AS REFERENCE
TO DETERMINE POSITIONING OF COMPONENTS WHEN BUILDING ASSEMBLY.
2. LEVELING FEET (8020 PN 2192) OPTIONAL.
3. EXTERIOR FOAM INSULATION (MMC PN 8694K54) NOT SHOWN. WRAP DOOR
AROUND THREE SIDES (NOT BOTTOM HINGE). INTERIOR DOOR FOAM (MMC
PN 93085K162) APPLIED ALONG ALL 4 EDGES OF DOOR INTERIOR. CUT TO
SUIT.
4. PLUG HOLE WITH MMC PN 9688K131 OR EQUIVALENT (TWO PLACES).
5. GLASS PLATE VIRTUAL PLANE TO BE PARALLEL TO VIRTUAL PLANE GENERATED
BY UPPER GIMBALL ASSY TO WITHIN +/- 0.010. THIS IS THE DOCUMENTED
WORST-CASE DEPTH OF FIELD FOR CAMERA USED FOR THE APPLICATION.
6. THOR LABS COMPONENTS TO BE SECURED WITH LOCTITE ONCE FINAL LED
POSITIONING HAS BEEN DETERMINED.
7. ENSURE ENCLOSURE IS LIGHT-TIGHT, AND FILL WITH TAPE OR RTV AROUND
JOINTS AND EDGES AS NECESSARY.
8. SECURE SET SCREW ON MS1/M THOR LABS 1CM ADJUSTOR WHEN ROUGH
CAMERA FOCUSING IS COMPLETED. REPLACE SET SCREW WITH MMC PN
9. SECURE DOOR HINGE TO FRONT PANEL WITH 10-32 BUTTON HEAD CAP
SCREW (MMC PN 92949A264), MOUNTING TO 8020 DROP-IN T-NUTS (PN
14164), 6 PLS.
10. SECURE DOOR HINGE TO DOOR BY THREADING M5 HARDWARE (MMC PN
91239A220) INTO M5 TAPPED HOLES IN DOOR, 6 PLS.

NOTES (CONT'D):
11. SECURE MAGNET SPACER BLOCK AND MAGNET CATCH TO FRONT PANEL
WITH M4 HARDWARE (MMC PN 91294A194 AND 93825A120).
12. SECURE MAGNET TO DOOR USING M4 HARDWARE (MMC PN 91294A188 AND
13. MODIFY MAGNET & CATCH THRU-HOLE (MMC PN 1745A12) AS NECESSARY
TO ENSURE HARDWARE IS FLUSH WITH MATING SURFACES.
14. BOM FOR LARVA TRACKER ASSEMBLY PROVIDED IN SEPARATE SPREADSHEET,
"BOM-211003-0001."

UNLESS OTHERWISE SPECIFIED:
DIMENSIONS ARE IN INCHES
.XXX
ANGLES
DO NOT SCALE DRAWING

KEY TECHNOLOGIES, INC
40 E CROSS ST., BALTIMORE, MD 21230
410-385-0200 WWW.KEYTECHINC.COM

PROPRIETARY AND CONFIDENTIAL
ANY REPRODUCTION IN PART OR AS A WHOLE WITHOUT THE WRITTEN PERMISSION OF KEY TECHNOLOGIES, INC. IS PROHIBITED.

THE INFORMATION CONTAINED IN THIS DRAWING IS THE SOLE PROPERTY OF KEY TECHNOLOGIES, INC.

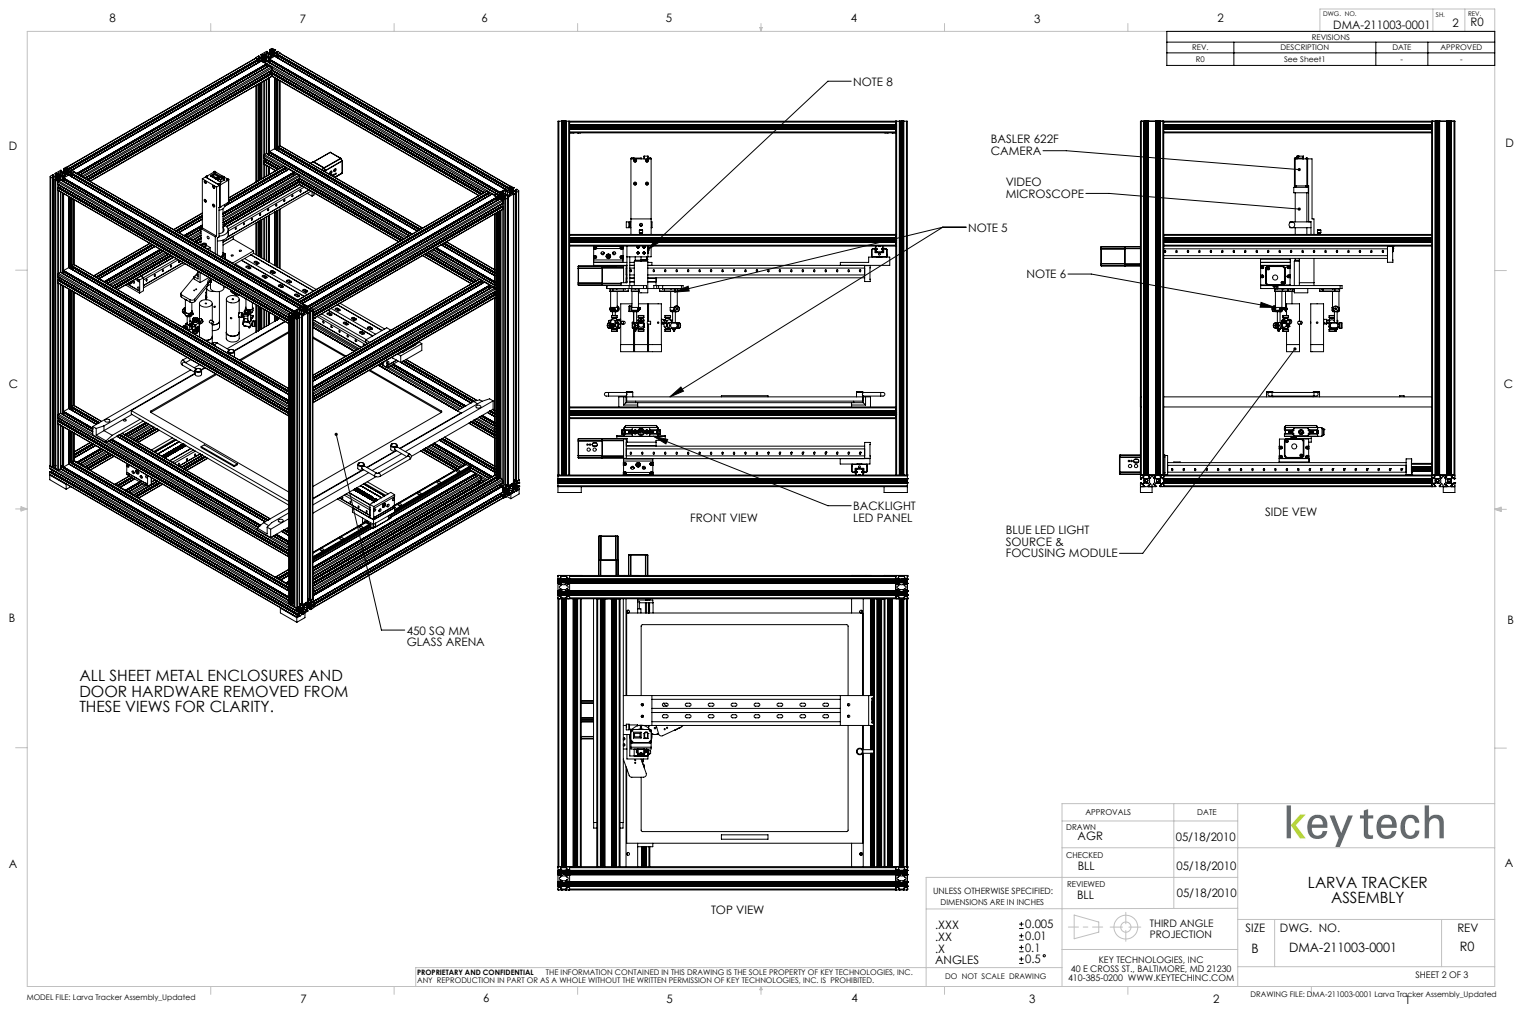
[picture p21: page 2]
NOTE 5; NOTE 8; FRONT VIEW; LED PANEL; TOP VIEW; NOTE 6; SIDE VEW; BASLER 622F; 450 SQ MM GLASS ARENA; DWG. NO.; REV; DMA-211003-0001; 2 R0 DWG. NO.; REV.; LARVA TRACKER ASSEMBLY 05/18/2010; THIRD ANGLE

REV. | DESCRIPTION | DATE | APPROVED
R0 | See Sheet1 | - | -

BLUE LED LIGHT
SOURCE &
FOCUSING MODULE

ALL SHEET METAL ENCLOSURES AND
DOOR HARDWARE REMOVED FROM
THESE VIEWS FOR CLARITY.

UNLESS OTHERWISE SPECIFIED:
DIMENSIONS ARE IN INCHES
.XXX

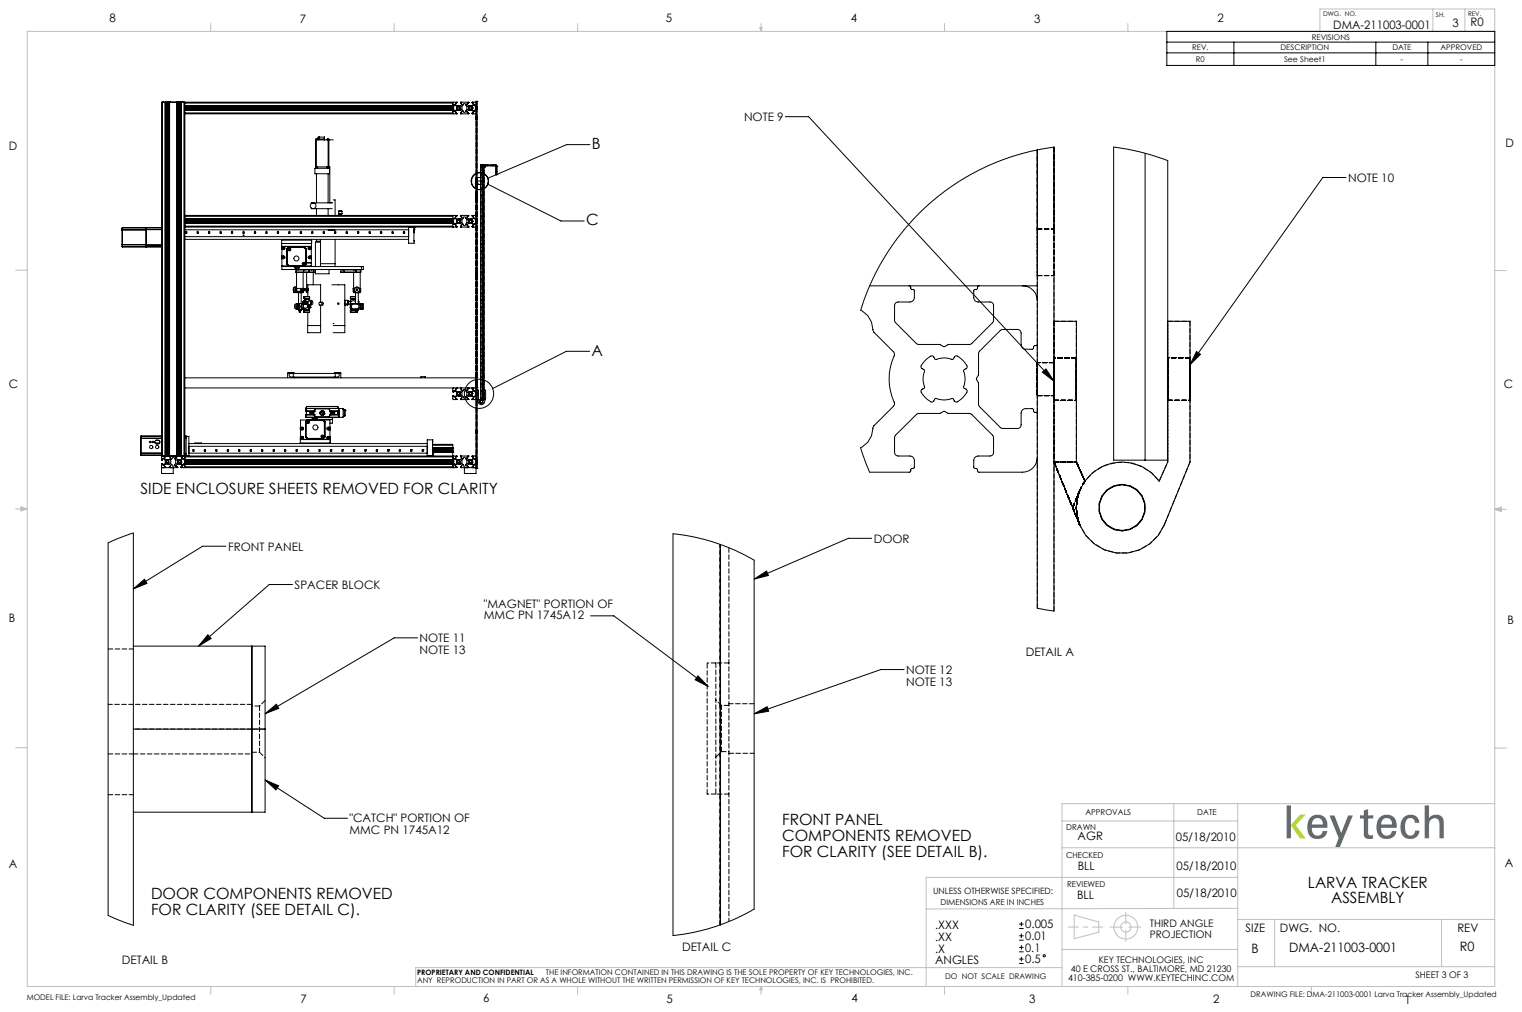
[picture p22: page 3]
DETAIL A; NOTE 9; NOTE 10; DETAIL B; NOTE 11 NOTE 13; FRONT PANEL; SPACER BLOCK; DETAIL C; NOTE 12 NOTE 13; DWG. NO.; REV; DMA-211003-0001; 3 R0 DWG. NO.; REV.; LARVA TRACKER ASSEMBLY 05/18/2010; THIRD ANGLE

REV. | DESCRIPTION | DATE | APPROVED
R0 | See Sheet1 | - | -

SIDE ENCLOSURE SHEETS REMOVED FOR CLARITY

"MAGNET" PORTION OF
MMC PN 1745A12

"CATCH" PORTION OF

FRONT PANEL
COMPONENTS REMOVED
FOR CLARITY (SEE DETAIL B).

DOOR COMPONENTS REMOVED
FOR CLARITY (SEE DETAIL C).

UNLESS OTHERWISE SPECIFIED:
DIMENSIONS ARE IN INCHES
.XXX

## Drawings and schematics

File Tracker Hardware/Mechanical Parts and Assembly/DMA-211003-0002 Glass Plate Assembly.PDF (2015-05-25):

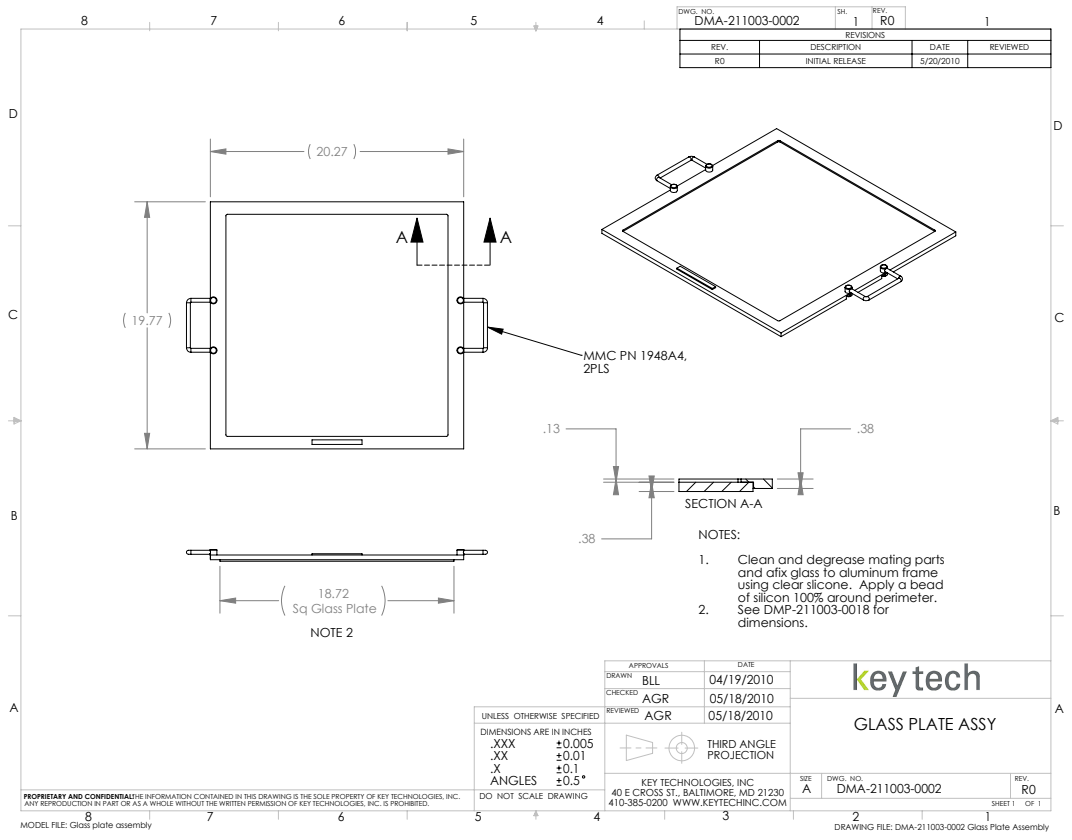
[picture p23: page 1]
Sq Glass Plate; MMC PN 1948A4,; NOTE 2; SIZE; DWG. NO.; SHEET 1 OF 1; 1 DWG. NO.; REV.; THIRD ANGLE

REV. | DESCRIPTION | DATE | REVIEWED
R0 | INITIAL RELEASE | 5/20/2010

SECTION A-A
NOTES:
1. Clean and degrease mating parts
and afix glass to aluminum frame
using clear slicone. Apply a bead
of silicon 100% around perimeter.
2. See DMP-211003-0018 for
dimensions.

REVIEWED UNLESS OTHERWISE SPECIFIED
DIMENSIONS ARE IN INCHES
.XXX
ANGLES
DO NOT SCALE DRAWING

GLASS PLATE ASSY

KEY TECHNOLOGIES, INC
40 E CROSS ST., BALTIMORE, MD 21230
410-385-0200 WWW.KEYTECHINC.COM

PROPRIETARY AND CONFIDENTIAL: THE INFORMATION CONTAINED IN THIS DRAWING IS THE SOLE PROPERTY OF KEY TECHNOLOGIES, INC.
ANY REPRODUCTION IN PART OR AS A WHOLE WITHOUT THE WRITTEN PERMISSION OF KEY TECHNOLOGIES, INC. IS PROHIBITED.
MODEL FILE: Glass plate assembly

DRAWING FILE: DMA-211003-0002 Glass Plate Assembly

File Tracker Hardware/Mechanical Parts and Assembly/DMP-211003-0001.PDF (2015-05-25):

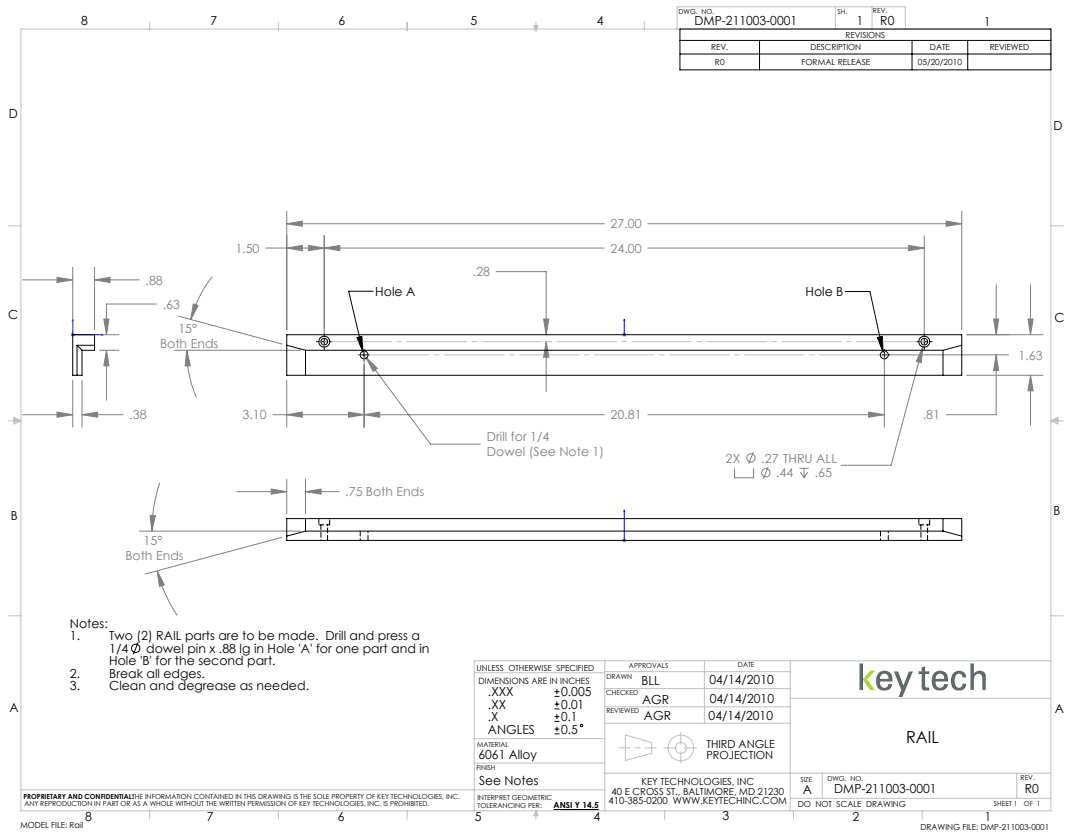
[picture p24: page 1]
Both Ends; .27 THRU ALL; Hole A; Hole B; .75 Both Ends; SIZE; DWG. NO.; SHEET 1 OF 1; 1 DWG. NO.; REV.; THIRD ANGLE; TOLERANCING PER:; ANSI Y 14.5

REV. | DESCRIPTION | DATE | REVIEWED
R0 | FORMAL RELEASE | 05/20/2010

Drill for 1/4
Dowel (See Note 1)

Notes:
1. Two (2) RAIL parts are to be made. Drill and press a
1/4 dowel pin x .88 lg in Hole 'A' for one part and in
Hole 'B' for the second part.
2. Break all edges.
3. Clean and degrease as needed.

UNLESS OTHERWISE SPECIFIED
DIMENSIONS ARE IN INCHES
.XXX
ANGLES
6061 Alloy
FINISH
See Notes
410-385-0200 WWW.KEYTECHINC.COM INTERPRET GEOMETRIC

KEY TECHNOLOGIES, INC
40 E CROSS ST., BALTIMORE, MD 21230

DO NOT SCALE DRAWING

PROPRIETARY AND CONFIDENTIAL: THE INFORMATION CONTAINED IN THIS DRAWING IS THE SOLE PROPERTY OF KEY TECHNOLOGIES, INC.
ANY REPRODUCTION IN PART OR AS A WHOLE WITHOUT THE WRITTEN PERMISSION OF KEY TECHNOLOGIES, INC. IS PROHIBITED.
MODEL FILE: Rail

DRAWING FILE: DMP-211003-0001

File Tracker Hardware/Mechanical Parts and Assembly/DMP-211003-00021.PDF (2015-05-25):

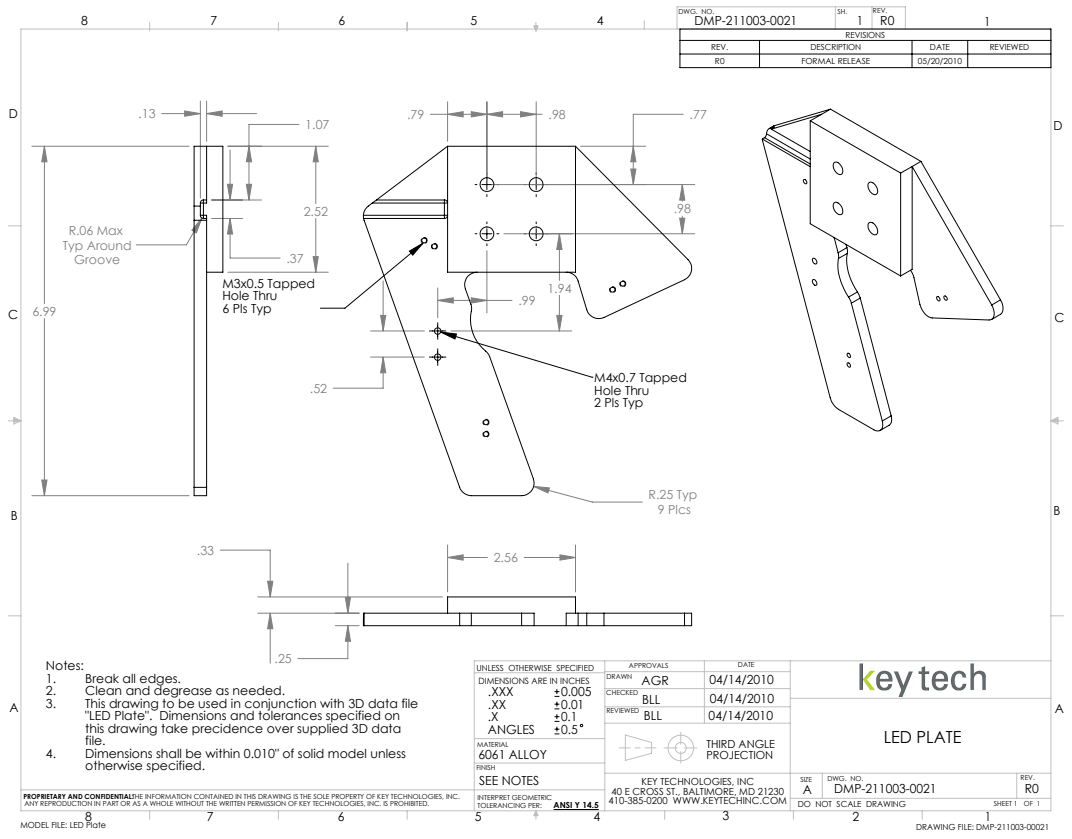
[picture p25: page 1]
R.25 Typ 9 Plcs; M3x0.5 Tapped; 1.94 Hole Thru; 6 Pls Typ; M4x0.7 Tapped Hole Thru 2 Pls Typ; R.06 Max Typ Around; SIZE; DWG. NO.; SHEET 1 OF 1; 1 DWG. NO.; REV.; LED PLATE; THIRD ANGLE; TOLERANCING PER:; ANSI Y 14.5

REV. | DESCRIPTION | DATE | REVIEWED
R0 | FORMAL RELEASE | 05/20/2010

Notes:
1. Break all edges.
2. Clean and degrease as needed.
3. This drawing to be used in conjunction with 3D data file

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

"LED Plate". Dimensions and tolerances specified on
this drawing take precidence over supplied 3D data
file.
4. Dimensions shall be within 0.010" of solid model unless
otherwise specified.

KEY TECHNOLOGIES, INC
40 E CROSS ST., BALTIMORE, MD 21230

DO NOT SCALE DRAWING

PROPRIETARY AND CONFIDENTIAL: THE INFORMATION CONTAINED IN THIS DRAWING IS THE SOLE PROPERTY OF KEY TECHNOLOGIES, INC.
ANY REPRODUCTION IN PART OR AS A WHOLE WITHOUT THE WRITTEN PERMISSION OF KEY TECHNOLOGIES, INC. IS PROHIBITED.
MODEL FILE: LED Plate

DRAWING FILE: DMP-211003-00021

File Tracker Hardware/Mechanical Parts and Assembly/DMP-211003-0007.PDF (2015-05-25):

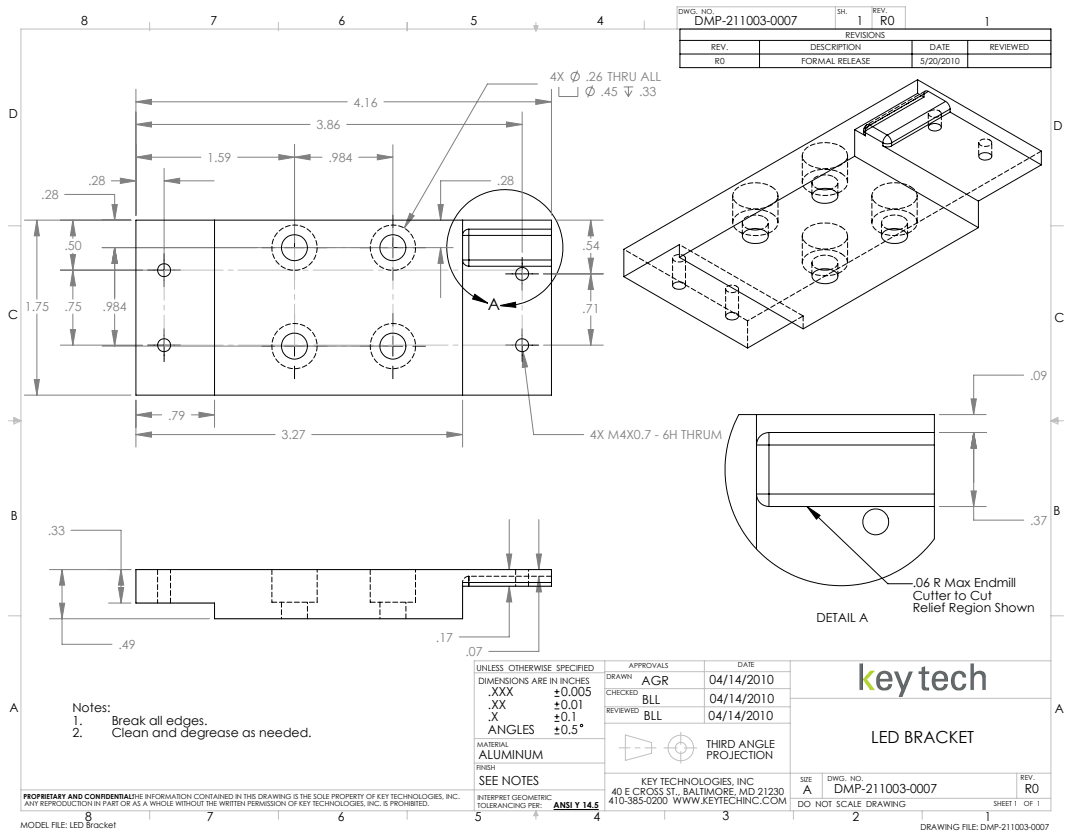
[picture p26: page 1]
.26 THRU ALL; 4X M4X0.7 - 6H THRUM; DETAIL A; SIZE; DWG. NO.; SHEET 1 OF 1; 1 DWG. NO.; REV.; LED BRACKET; THIRD ANGLE; TOLERANCING PER:; ANSI Y 14.5

REV. | DESCRIPTION | DATE | REVIEWED
R0 | FORMAL RELEASE | 5/20/2010

.06 R Max Endmill
Cutter to Cut
Relief Region Shown

UNLESS OTHERWISE SPECIFIED
DIMENSIONS ARE IN INCHES
.XXX
ANGLES
ALUMINUM
FINISH
SEE NOTES
410-385-0200 WWW.KEYTECHINC.COM INTERPRET GEOMETRIC

Notes:
1. Break all edges.
2. Clean and degrease as needed.

KEY TECHNOLOGIES, INC
40 E CROSS ST., BALTIMORE, MD 21230

DO NOT SCALE DRAWING

PROPRIETARY AND CONFIDENTIAL: THE INFORMATION CONTAINED IN THIS DRAWING IS THE SOLE PROPERTY OF KEY TECHNOLOGIES, INC.
ANY REPRODUCTION IN PART OR AS A WHOLE WITHOUT THE WRITTEN PERMISSION OF KEY TECHNOLOGIES, INC. IS PROHIBITED.
MODEL FILE: LED Bracket

DRAWING FILE: DMP-211003-0007

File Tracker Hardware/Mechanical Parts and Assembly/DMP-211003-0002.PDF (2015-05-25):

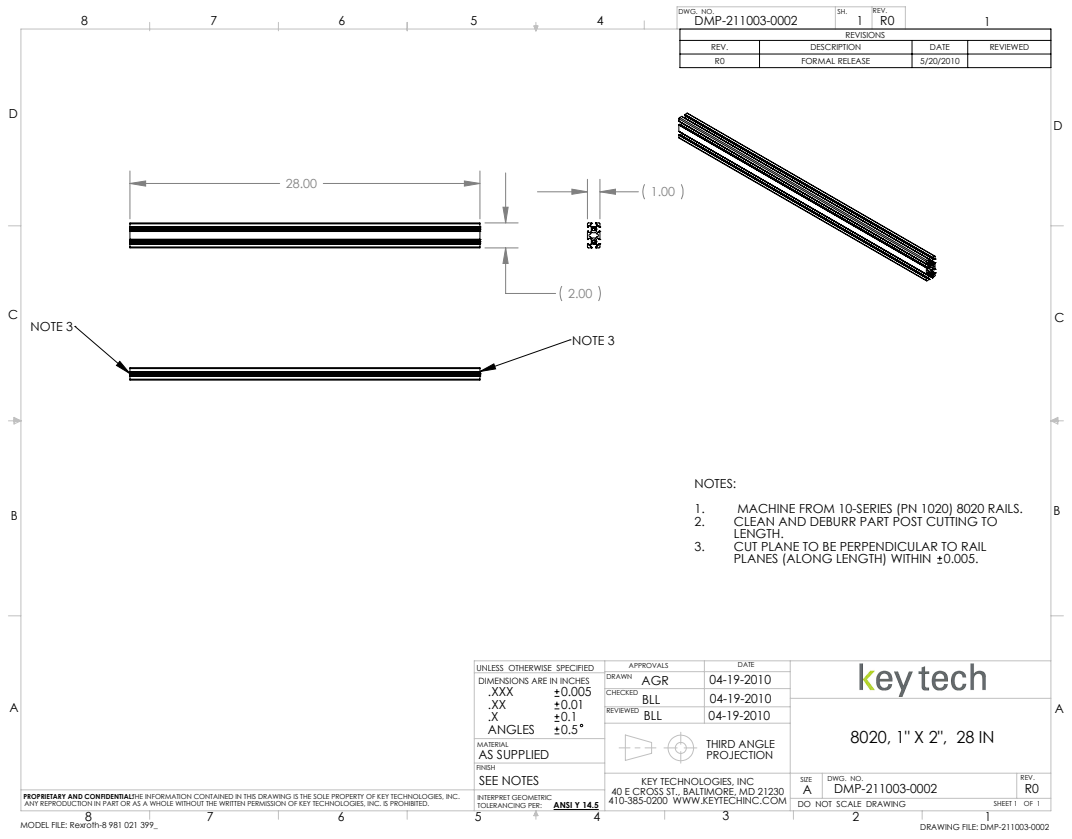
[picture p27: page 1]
NOTE 3; SIZE; DWG. NO.; SHEET 1 OF 1; 1 DWG. NO.; REV.; THIRD ANGLE; TOLERANCING PER:; ANSI Y 14.5

REV. | DESCRIPTION | DATE | REVIEWED
R0 | FORMAL RELEASE | 5/20/2010

NOTES:
1. MACHINE FROM 10-SERIES (PN 1020) 8020 RAILS.
2. CLEAN AND DEBURR PART POST CUTTING TO
LENGTH.
3. CUT PLANE TO BE PERPENDICULAR TO RAIL
PLANES (ALONG LENGTH) WITHIN 0.005.

UNLESS OTHERWISE SPECIFIED
DIMENSIONS ARE IN INCHES
.XXX
ANGLES
AS SUPPLIED
FINISH
SEE NOTES
410-385-0200 WWW.KEYTECHINC.COM INTERPRET GEOMETRIC

KEY TECHNOLOGIES, INC
40 E CROSS ST., BALTIMORE, MD 21230

DO NOT SCALE DRAWING

PROPRIETARY AND CONFIDENTIAL: THE INFORMATION CONTAINED IN THIS DRAWING IS THE SOLE PROPERTY OF KEY TECHNOLOGIES, INC.
ANY REPRODUCTION IN PART OR AS A WHOLE WITHOUT THE WRITTEN PERMISSION OF KEY TECHNOLOGIES, INC. IS PROHIBITED.
MODEL FILE: Rexroth-8 981 021 399_

DRAWING FILE: DMP-211003-0002

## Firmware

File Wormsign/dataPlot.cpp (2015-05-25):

#include "dataPlot.h"
#include "experimentAgent.h"
#include "analysisModule.h"
#include "stimThread.h"
#include "stageThread.h"
#include "coreCamThread.h"

DataPlot::DataPlot(Wormsign * ui):QWidget((QWidget*)ui){

	this->setAutoFillBackground(true);
	this->setPalette(QPalette(QColor(200,180,180)));

	gui = ui;

	historyDepth = 600;
	plotData.resize(historyDepth);
	stimData.resize(historyDepth);

	parameterList = new QComboBox(this);
	parameterList->setGeometry(10,10,200,20);
	QStringList parameters;
	parameters << "Head to Body Angle (deg)";
	parameters << "Body Bearing (deg)";
	parameters << "Head Speed (mm/s)";
	parameters << "Tail Speed (mm/s)";
	parameters << "Body Bearing Derivative (deg/s)";
	parameterList->insertItems(0,parameters);



};
DataPlot::~DataPlot(){};

void DataPlot::paintEvent(QPaintEvent *){
	
	QPainter painter(this);
	double xval, yval, tickVal, tickStep;
	int nTicks;
	
	//Draw Graph frame
	double width = geometry().width();
	double height = geometry().height();
	double left = width*.1;
	double right = width*.9;
	double top = height*.2;
	double bottom = height*.85;

	double yOffset, yTickStep;
	switch(parameterList->currentIndex()){
		case 0: // "Head to Body Angle (deg)"
			yOffset = -180;
			yTickStep = 90;
			break;
		case 1: // "Body Bearing (deg)"
			yOffset = -180;
			yTickStep = 90;
			break;
		case 2: // "Head Velocity (mm/s)"
			yOffset = 0;
			yTickStep = 2;
			break;
		case 3: // "Tail Velocity (mm/s)"
			yOffset = 0;
			yTickStep = 2;
			break;
		case 4: // "Body Bearing Derivative (deg/s)
			yOffset = -30;
			yTickStep = 15;
			break;
	}

	//left vertical bar
	painter.drawLine(left,top,left,bottom);
	//right bar = axis w/ labels (ms)
	painter.drawLine(right,top,right,bottom);
	yval = bottom;
	xval = right;
	tickVal = 0;
	nTicks = 5;
	while(yval > top){
		painter.setPen(QColor(0,0,0));
		painter.drawLine(xval,yval,xval-10,yval);
		painter.drawText(xval+5,yval+5,QString().sprintf("%.0f",tickVal+yOffset));
		
		//draw dashed grid lines
		if(yval != bottom){
			painter.setPen(QPen(QBrush(QColor(100,100,100)),1,Qt::DashLine));
			painter.drawLine(left,yval,right,yval);
		}

		yval -= (bottom-top)/double(nTicks);
		tickVal += yTickStep; //10ms steps
	}
	double yscale = (bottom - yval)/tickVal;
	
	painter.setPen(QPen(QBrush(QColor(0,0,0)),1,Qt::SolidLine));

	//bottom bar = axis w/ labels (time)
	painter.drawLine(left,bottom,right,bottom);
	yval = bottom;
	xval = right;
	tickVal = 0;
	nTicks = 5;
	tickStep = floor( .5 + (double(historyDepth*gui->frameIntIn->value())/1000.0)/double(nTicks));  //round
	double xStep = (right-left)*tickStep/(double(historyDepth*gui->frameIntIn->value())/1000.0);
		
	while(xval>left){
		painter.drawLine(xval,yval,xval,yval-10);
		painter.drawText(xval-2,yval+12,QString().sprintf("%.0f",tickVal));
		xval -= xStep;  //calculate steps
		tickVal += tickStep;
	}
	
	painter.drawText(width*.4,bottom + height*.1,QString("History (sec)"));

	//painter.rotate(-90);
	//painter.drawText(-height*.7,width*.99,QString("Closed Loop Time (ms)"));
	//painter.rotate(90);

	//if not data available, return
	if(!gui->expAgent) return;
	if(!gui->camThread) return;

	double tickPerMMX = gui->stageThread->tickPerMM_X;
	double tickPerMMY = gui->stageThread->tickPerMM_Y;
	double umPerPixel = gui->camThread->umPerPixel;


	//build data
	if(plotData.size() != historyDepth) plotData.resize(historyDepth);
	if(stimData.size() != historyDepth) stimData.resize(historyDepth);
	xStep = (right-left)/plotData.size();
	xval = left;
	int indRoot = gui->stimThread->index - historyDepth;
	int ind;
	double accumulator;
	double normFactor = 0;
	double filterHistory = 60;
	for(int i=1; i<=filterHistory; i++) normFactor+=i;

	int headAngleHistoryStep = 1;
	double dt = double(headAngleHistoryStep*gui->expAgent->analysisMod->frameIntervalMS)/1000.0; //time interval into history in seconds

	for(int i=0; i<historyDepth; i++){
		ind = indRoot + i;
		if(ind < 0){
			yval = bottom;
		}else{
			switch(parameterList->currentIndex()){
				case 0: // "Head to Body Angle (deg)"
					yval = gui->expAgent->analysisMod->headToBodyAngle[ind % gui->expAgent->analysisMod->nBuffers]*180/M_PI - yOffset;
					yval = bottom - yval*yscale;
					break;
				case 1: // "Body Bearing (deg)"
					//yval = gui->expAgent->analysisMod->tailBearingAngle[ind % gui->expAgent->analysisMod->nBuffers]*180/M_PI - yOffset;
					yval = gui->expAgent->analysisMod->newTailBearing[ind % gui->expAgent->analysisMod->nBuffers]*180/M_PI - yOffset;
					yval = bottom - yval*yscale;
					break;
				case 2: // "Head Speed (mm/s)"
					yval = gui->expAgent->analysisMod->headSpeed[ind % gui->expAgent->analysisMod->nBuffers] - yOffset;
					yval = bottom - yval*yscale;
					break;
				case 3: // "Tail Speed (mm/s)"
					yval = gui->expAgent->analysisMod->tailSpeed[ind % gui->expAgent->analysisMod->nBuffers] - yOffset;
					yval = bottom - yval*yscale;
					break;
				case 4: // "Body Bearing Derivative (deg/s)

					yval = gui->expAgent->analysisMod->dNewTailBearing[ind % gui->expAgent->analysisMod->nBuffers]*180/M_PI;
					yval = bottom - (yval-yOffset)*yscale;
					break;
			}
			
		}
		//scale raw value to graphics
		plotData[i].setX(xval);
		plotData[i].setY(yval);
		
		xval += xStep;
	}

	//Plot stimulus in blue
	xval = left;
	yscale = (bottom-top)/100;
	for(int i=0; i<historyDepth; i++){
		ind = indRoot+i;
		if(ind < 0){
			yval = bottom;
		}else{
			ind = ind%gui->stimThread->stimAmps.size();
			yval = gui->stimThread->stimAmps[ind];
			yval = bottom - yval*yscale;
		}
		stimData[i].setX(xval);
		stimData[i].setY(yval);
		xval += xStep;
	}

	//plot stimulus in back in blue
	painter.setPen(QColor(0,0,200));
	painter.drawPolyline(stimData);

	//Plot Data in dark green
	painter.setPen(QColor(0,150,0));
	painter.drawPolyline(plotData);

	
};

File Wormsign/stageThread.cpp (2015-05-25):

#include "stageThread.h"
#include "experimentAgent.h"
#include "analysisModule.h"

StageThread::StageThread(Wormsign * ui){
	exited = true;
	stopped = true;

	gui = ui;
	comName = QString("COM3");  //default
	
	//From Calibration
	tickPerMM_X = 2007;
	tickPerMM_Y = 2032;

	xpos = 0; ypos = 0; xposMM = 0; yposMM = 0;
	state = NONE;

	vel = 0; accel = 0;

};
StageThread::~StageThread(){stop();};

//Blocking cyclick polling to control motor and retrieve position
void StageThread::run(){
	
	index = -1;
	if(!connectCOM()) {stopped = true; return;}
	int nextInd;
	double dx, dy;

	//if values haven't been read yet, read them out
	if(vel == 0){
		vel = readVelocityTarget();
		accel = readAcceleration();
	}else{
		//otherwise, apply the values from the UI
		//initial value was 4687
		setVelocityTarget(vel);
		//initial value was 50
		setAcceleration(accel);

		vel = readVelocityTarget();
		accel = readAcceleration();

	}

	LARGE_INTEGER pcTic, pcToc, pcFreq;
	double diff;
	QueryPerformanceFrequency(&pcFreq);
	
	stopped = false;
	exited = false;

	while(!stopped){
		
		switch(state){
			case NONE:
				Sleep(10);
				break;
			case HOME:
				sendHome();
				state = NONE;
				break;
			case POLLPOSOTION:  //Simply poll stage position 
				PurgeComm(hCom,PURGE_RXCLEAR);
				pollPosition();
				emit posUpdate();
				break;

			case EXPERIMENT:  //Send movement commands and poll position
				if(!gui->expAgent) continue; //should not be the case, the expagent put it in this mode
				if(gui->expAgent->analysisMod->index == -1) continue;
				
				QueryPerformanceCounter(&pcTic);
				//request position
				pollPosition();
								
				//send move command from latest analysis frame (don't need to do it for every one)	
				nextInd = (gui->expAgent->analysisMod->index)%gui->expAgent->analysisMod->nBuffers;
				
				//Calculate difference in image in pixels
				dx = (double(gui->expAgent->analysisMod->centroid[nextInd].x) - double(gui->camThread->width)/2.0);
				dy = (double(gui->expAgent->analysisMod->centroid[nextInd].y) - double(gui->camThread->height)/2.0);
				//convert from pixels to mm 
				dx *= gui->camThread->umPerPixel/1000.0;
				dy *= gui->camThread->umPerPixel/1000.0;
				//convert from mm to motor steps
				dx *= tickPerMM_X;
				dy *= tickPerMM_Y;
					
				//Calibration doesn't seem to match, causing overshoot
				// Instead, only command the stage to go part of the way to target, this will converge to the 
				// final desired position
				dx *= .5;
				dy *= .5;
				Sleep(10);
				if(abs(dx) > 100 | abs(dy) > 100)
					sendRelativeMove(int(dx),int(dy));
				
				//fastPacket(int(dx), int(dy));
				QueryPerformanceCounter(&pcToc);
				
				//Profiled time to communicate with the stage
				diff = 1000.0*double(pcToc.QuadPart-pcTic.QuadPart)/double(pcFreq.QuadPart);

				emit posUpdate();
				break;
		}
	}

	disconnectCOM();
	
	exited = true;
};
void StageThread::stop(){
	stopped = true;
	while(!exited){
		stopped = true;
		Sleep(1);
	}
};

void StageThread::sendHome(){
	cBuf[0]=0; cBuf[1]=1; cBuf[2]=0; cBuf[3]=0; cBuf[4]=0; cBuf[5]=0;
	WriteFile(hCom,cBuf,6,&txBytes,NULL);
};

void StageThread::setVelocityTarget(int vTarget){

	//initial value was 4687
	uchar * cptr = (uchar*)&vTarget;
	ucBuf[0] = 23; ucBuf[1] = 42; ucBuf[2] = cptr[0]; ucBuf[3] = cptr[1]; ucBuf[4] = cptr[2]; ucBuf[5] = cptr[3];
	WriteFile(hCom,ucBuf,6,&txBytes,NULL);
	Sleep(25);
	//ucBuf[0] = 3;
	//WriteFile(hCom,ucBuf,6,&txBytes,NULL);
	Sleep(25);
	ucBuf[0] = 45;
	WriteFile(hCom,ucBuf,6,&txBytes,NULL);
	Sleep(25);
	//ucBuf[0] = 5;
	//WriteFile(hCom,ucBuf,6,&txBytes,NULL);
	Sleep(25);

};


int StageThread::readVelocityTarget(){
	int command = 42;
	uchar *cptr = (uchar*)&command;
	Sleep(100);
	PurgeComm(hCom,PURGE_RXCLEAR);

	ucBuf[0] = 2; ucBuf[1] = 53; ucBuf[2] = cptr[0]; ucBuf[3] = cptr[1]; ucBuf[4] = cptr[2]; ucBuf[5] = cptr[3];
	WriteFile(hCom,ucBuf,6,&txBytes,NULL);
	ReadFile(hCom,ucBuf,6,&rxBytes,NULL);
	
	//qDebug("%d,%d,%d,%d,%d,%d",ucBuf[0],ucBuf[1],ucBuf[2],ucBuf[3],ucBuf[4],ucBuf[5]);

	cptr = &ucBuf[2];
	command = *((int*)cptr);

	return command;
};

void StageThread::setAcceleration(int accel){

	//initial value was 50
	uchar * cptr = (uchar*)&accel;
	ucBuf[0] = 23; ucBuf[1] = 43; ucBuf[2] = cptr[0]; ucBuf[3] = cptr[1]; ucBuf[4] = cptr[2]; ucBuf[5] = cptr[3];
	WriteFile(hCom,ucBuf,6,&txBytes,NULL);
	Sleep(25);
	//ucBuf[0] = 3;
	//WriteFile(hCom,ucBuf,6,&txBytes,NULL);
	Sleep(25);
	ucBuf[0] = 45;
	WriteFile(hCom,ucBuf,6,&txBytes,NULL);
	Sleep(25);
	//ucBuf[0] = 5;
	//WriteFile(hCom,ucBuf,6,&txBytes,NULL);
	Sleep(25);
}

int StageThread::readAcceleration(){
	int command = 43;
	uchar *cptr = (uchar*)&command;

	Sleep(100);
	PurgeComm(hCom,PURGE_RXCLEAR);
	ucBuf[0] = 2; ucBuf[1] = 53; ucBuf[2] = cptr[0]; ucBuf[3] = cptr[1]; ucBuf[4] = cptr[2]; ucBuf[5] = cptr[3];
	WriteFile(hCom,ucBuf,6,&txBytes,NULL);
	ReadFile(hCom,ucBuf,6,&rxBytes,NULL);

	cptr = &ucBuf[2];
	command = *((int*)cptr);

	return command;
}


void StageThread::pollPosition(){

	//PurgeComm(hCom,PURGE_RXCLEAR);

	//request position, stage 4
	posReq[0] = 4; posReq[1] = 60;  
	WriteFile(hCom,posReq,6,&txBytes,NULL);
	ReadFile(hCom,ucBuf,6,&rxBytes,NULL);
	while(ucBuf[1] != 60){
		//qDebug("Bad x: %d, %d, %d, %d, %d, %d",ucBuf[0],ucBuf[1],ucBuf[2],ucBuf[3],ucBuf[4],ucBuf[5]);
		ReadFile(hCom,ucBuf,6,&rxBytes,NULL);
		if(rxBytes == 0) break;
	}

	xpos = 256*256*256*((unsigned int)ucBuf[5])+256*256*((unsigned int)ucBuf[4])+
		256*((unsigned int)ucBuf[3])+((unsigned int)ucBuf[2]);
	xposMM = double(xpos)/tickPerMM_X;
	
	//qDebug("x: %d, %d, %d, %d, %d, %d",ucBuf[0],ucBuf[1],ucBuf[2],ucBuf[3],ucBuf[4],ucBuf[5]);
	
	
	//Request position, stage 2 y-position
	posReq[0] = 2; posReq[1] = 60;  
	WriteFile(hCom,posReq,6,&txBytes,NULL);
	ReadFile(hCom,ucBuf,6,&rxBytes,NULL);
	
	while(ucBuf[1] != 60){
		//qDebug("Bad y: %d, %d, %d, %d, %d, %d",ucBuf[0],ucBuf[1],ucBuf[2],ucBuf[3],ucBuf[4],ucBuf[5]);
		ReadFile(hCom,ucBuf,6,&rxBytes,NULL);
		if(rxBytes == 0) break;
	}

	ypos = 256*256*256*((unsigned int)ucBuf[5])+256*256*((unsigned int)ucBuf[4])+
		256*((unsigned int)ucBuf[3])+((unsigned int)ucBuf[2]);
	yposMM = double(ypos)/tickPerMM_Y;

	//qDebug("y: %d, %d, %d, %d, %d, %d",ucBuf[0],ucBuf[1],ucBuf[2],ucBuf[3],ucBuf[4],ucBuf[5]);
};

void StageThread::sendRelativeMove(int dx, int dy){

	//PurgeComm(hCom,PURGE_RXCLEAR);
	int i;
	uchar * cptr;

	cptr = (uchar*)&dx;
	i=0;
	ucBuf[i+0] = 45;  ucBuf[i+1] = 21; ucBuf[i+2] = cptr[0]; ucBuf[i+3] = cptr[1]; ucBuf[i+4] = cptr[2]; ucBuf[i+5] = cptr[3];
	i=6;
	cptr = (uchar*)&dy;
	ucBuf[i+0] = 23;  ucBuf[i+1] = 21; ucBuf[i+2] = cptr[0]; ucBuf[i+3] = cptr[1]; ucBuf[i+4] = cptr[2]; ucBuf[i+5] = cptr[3];

	WriteFile(hCom,ucBuf,12,&txBytes,NULL);

};

void StageThread::fastPacket(int dx, int dy){

	bool xComplete = false;
	bool yComplete = false;
	uchar * cptr;
	int i;

	//request position, stage 4 - xpos
	ucBuf[0] = 4; ucBuf[1] = 60;  
	//request position, stage 2 - ypos
	ucBuf[6] = 2; ucBuf[7] = 60;  

	//Send dx
	cptr = (uchar*)&dx;
	i=12;
	ucBuf[i+0] = 45;  ucBuf[i+1] = 21; ucBuf[i+2] = cptr[0]; ucBuf[i+3] = cptr[1]; ucBuf[i+4] = cptr[2]; ucBuf[i+5] = cptr[3];
	//send dy
	cptr = (uchar*)&dy;
	i=18;
	ucBuf[i+0] = 23;  ucBuf[i+1] = 21; ucBuf[i+2] = cptr[0]; ucBuf[i+3] = cptr[1]; ucBuf[i+4] = cptr[2]; ucBuf[i+5] = cptr[3];

	int nTransmit = 24;
	if(abs(dx) < 200 & abs(dy) < 200) nTransmit = 12;  //Only send pos request

	WriteFile(hCom,ucBuf,nTransmit,&txBytes,NULL);
	rxBytes = 1;
	while((!xComplete & !yComplete) | rxBytes == 0){
		oneRead[1] = 0;
		ReadFile(hCom,oneRead,6,&rxBytes,NULL); //read single response
		if(oneRead[1] == 60){
			if(oneRead[0] == 4){ //xpos
				xpos = 256*256*256*((unsigned int)oneRead[5])+256*256*((unsigned int)oneRead[4])+
						256*((unsigned int)oneRead[3])+((unsigned int)oneRead[2]);
				xposMM = double(xpos)/tickPerMM_X;
				xComplete = true;
			}
			if(oneRead[0] == 2){  //ypos
				ypos = 256*256*256*((unsigned int)oneRead[5])+256*256*((unsigned int)oneRead[4])+
					256*((unsigned int)oneRead[3])+((unsigned int)oneRead[2]);
				yposMM = double(ypos)/tickPerMM_Y;
				yComplete = true;
			}
		}
	}





};


//Provide a string list of names of valid COM ports
//Will not return a port if it is connected in another application
QStringList StageThread::enumeratePorts(){
	
	QStringList outList;
	HANDLE h;
	QString tempName;

	for(int i=0; i<15; i++){
		tempName.sprintf("COM%d",i);
		//Try to open this COMi
		h = CreateFile(tempName.utf16(),GENERIC_READ|GENERIC_WRITE,0,0,OPEN_EXISTING,0,0);
		if(h!=INVALID_HANDLE_VALUE) {
			outList << tempName;
			CloseHandle(h); //release port
		}
	}

	return outList;
};
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
